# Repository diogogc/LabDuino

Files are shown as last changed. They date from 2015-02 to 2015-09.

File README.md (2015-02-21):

# LabDuino
###EN
This project is my contribution STEM driven classes, in order to help teachers and students on science learning. It's an Arduino based project, feel free to fork or contribute to make it better, or just download, build it yourself or on your classes.

Main Components:

- 1 x Arduino Pro Mini 328 5V;

- 2 x PCF8574P Port expander;

- 1x 16x2 Display;

Voltage Regulator:

I actually followed this instructables for that: <http://www.instructables.com/id/Portable-5V-Regulator/>

I just changed the 78L05 with L7805CV, because i already had a few of them around.

Other

- 8 x 10k Ohms resistor

- 4 x 330 Ohms resistor

- 10k Ohms trimpot

- 2 x 16 pins IC socket (for PCF8574P);

- 16 vias flat 28AWG cable

- 8 x headphone jack (we gonna use it to connect sensors)

For more information, please check the Wiki page.

If you want to become a collaborator, please fill this form:
http://goo.gl/dhk8Ny

###PT-br
Este Projeto é minha contribição para aulas voltadas a STEM, para ajudar professores e alunos no aprendizado de ciências. É um projeto baseado em arduino. Sinta-se livre para fazer fork ou contribuir para fazer este projeto melhor, ou apenas baixe e construa e utilize em suas turmas.

Componentes Principais:

- 1 x Arduino Pro Mini 328 5V;

- 2 x PCF8574P Port expander;

- 1x 16x2 Display;

Regulador de Voltagem:

Eu segui as seguintes instruções: <http://www.instructables.com/id/Portable-5V-Regulator/>

Eu mudei o 78L05 pelo L7805CV porque já tinha alguns aqui comigo.

Outros

- 8 x 10k Ohms resistor

- 4 x 330 Ohms resistor

- 10k Ohms trimpot

- 2 x 16 pinos CI socket (para o PCF8574P);

- Cabo de 16 vias flat 28AWG

- 8 x headphone jack (Usado para conectar os sensores)

Para mais informações, porfavor consulte a pagina Wiki.

Se você quiser se tornar um colaborador, porfavor preencha este formulário:
http://goo.gl/dhk8Ny

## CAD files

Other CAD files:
LaserCutterFiles/LabDuinoBox.skp

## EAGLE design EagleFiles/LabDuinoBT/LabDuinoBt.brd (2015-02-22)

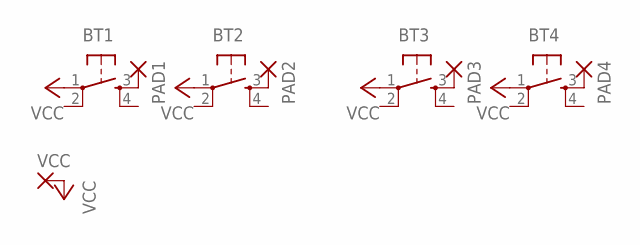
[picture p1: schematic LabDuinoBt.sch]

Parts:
BT1, BT2, BT3, BT4: TAC_SWITCHPTH; TACTILE-PTH
PAD1, PAD2, PAD3, PAD4: 1,6/0,9
VCC: 1,6/0,9

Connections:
unnamed: BT1.3, PAD1.1
unnamed: BT2.3, PAD2.1
unnamed: BT3.3, PAD3.1
unnamed: BT4.3, PAD4.1
VCC: BT1.1, BT2.1, BT3.1, BT4.1, VCC.1

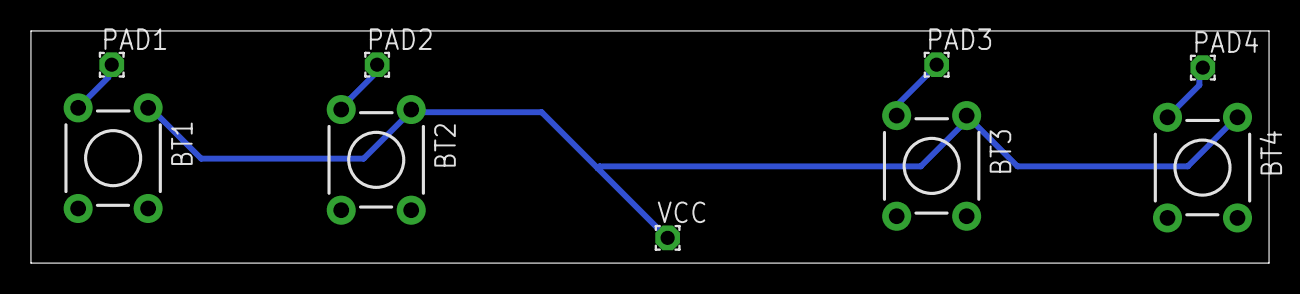
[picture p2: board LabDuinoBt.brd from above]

Board: 2 copper layers, 80.0 x 15.0 mm, 9 parts (0 on the bottom side), 5 nets.

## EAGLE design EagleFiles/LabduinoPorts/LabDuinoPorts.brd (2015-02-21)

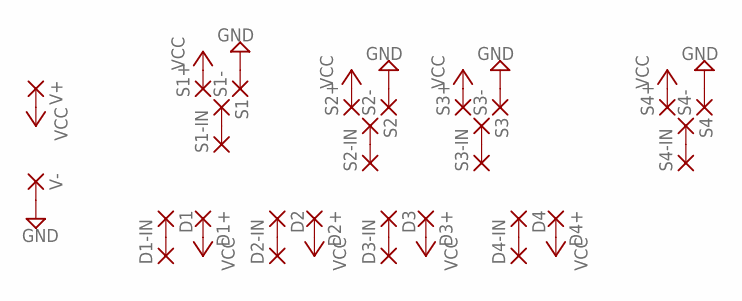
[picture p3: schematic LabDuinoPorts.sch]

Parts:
D1, D1+, D1-IN, D2, D2+, D2-IN, D3, D3+, D3-IN, D4, D4+, D4-IN: 2,54/0,9
S1, S1+, S1-, S1-IN, S2, S2+, S2-, S2-IN, S3, S3+, S3-, S3-IN, S4, S4+, S4-, S4-IN: 2,54/0,9
V+: 2,54/0,9
V-: 2,54/0,9

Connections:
GND: S1-.1, S2-.1, S3-.1, S4-.1, V-.1
unnamed: S1.1, S1-IN.1
unnamed: S2.1, S2-IN.1
unnamed: S3.1, S3-IN.1
unnamed: S4.1, S4-IN.1
unnamed: D1.1, D1-IN.1
unnamed: D2.1, D2-IN.1
unnamed: D3.1, D3-IN.1
unnamed: D4.1, D4-IN.1
VCC: D1+.1, D2+.1, D3+.1, D4+.1, S1+.1, S2+.1, S3+.1, S4+.1, V+.1

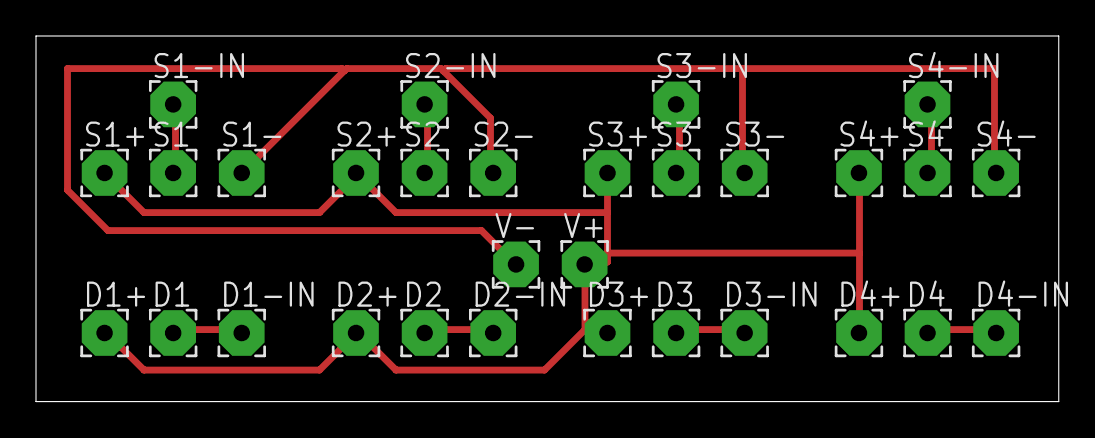
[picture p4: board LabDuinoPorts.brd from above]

Board: 2 copper layers, 56.8 x 20.3 mm, 30 parts (0 on the bottom side), 10 nets.

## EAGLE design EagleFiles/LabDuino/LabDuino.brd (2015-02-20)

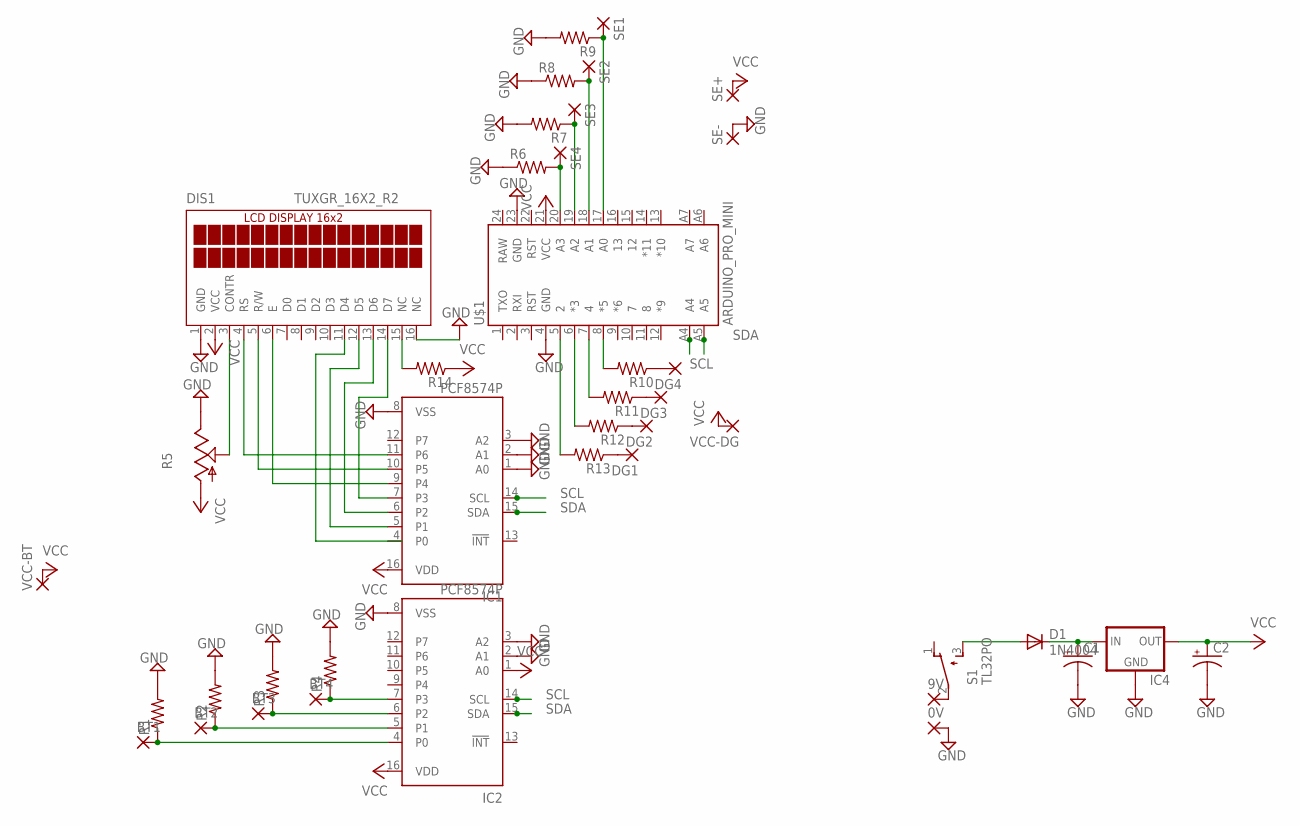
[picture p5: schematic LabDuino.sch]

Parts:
0V, 9V: 2,54/1,1
BT1, BT2, BT3, BT4: 1,6/0,9
C1, C2: CPOL-USE2-4; E2-4
D1: 1N4004; DO41-10
DG1, DG2, DG3, DG4: 1,6/0,9
DIS1: TUXGR_16X2_R2
IC1, IC2: PCF8574P; DIL16
IC4: V_REG_78XX-TO-220; TO-220-ALT
R1, R2, R3, R4, R10, R11, R12, R13, R14: RESISTORPTH-1/6W; 1/6W-RES
R5: TRIM_US-RS3; RS3
R6, R7, R8, R9: R-US_0204/7; 0204/7
S1: TL32PO; TL3XPO
SE1, SE2, SE3, SE4: 1,6/0,9
SE+: 1,6/0,9
SE-: 1,6/0,9
U$1: ARDUINO_PRO_MINI
VCC-BT: 1,6/0,9
VCC-DG: 1,6/0,9

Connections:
10K: BT2.1, IC2.5 (P1), R2.1
GND: 0V.1, C1.-, C2.-, DIS1.1 (GND), DIS1.16 (NC), IC1.1 (A0), IC1.2 (A1), IC1.3 (A2), IC1.8 (VSS), IC2.2 (A1), IC2.3 (A2), IC2.8 (VSS), IC4.GND, R1.2, R2.2, R3.2, R4.2, R5.E, R6.1, R7.2, R8.1, R9.2, SE-.1, U$1.4 (GND), U$1.23 (GND)
unnamed: R6.2, SE4.1, U$1.20 (A3)
unnamed: BT1.1, IC2.4 (P0), R1.1
unnamed: 9V.1, S1.2
unnamed: BT3.1, IC2.6 (P2), R3.1
unnamed: BT4.1, IC2.7 (P3), R4.1
unnamed: R7.1, SE3.1, U$1.19 (A2)
unnamed: DIS1.4 (RS), IC1.11 (P6)
unnamed: DIS1.5 (R/W), IC1.10 (P5)
unnamed: DIS1.6 (E), IC1.9 (P4)
unnamed: DIS1.14 (D7), IC1.7 (P3)
unnamed: DIS1.13 (D6), IC1.6 (P2)
unnamed: DIS1.12 (D5), IC1.5 (P1)
unnamed: DIS1.3 (CONTR), R5.S
unnamed: D1.A, S1.3 (S)
unnamed: C1.+, D1.C, IC4.IN
unnamed: R8.2, SE2.1, U$1.18 (A1)
unnamed: R9.1, SE1.1, U$1.17 (A0)
unnamed: R13.2, U$1.5 (2)
unnamed: R12.2, U$1.6 (*3)
unnamed: R11.2, U$1.7 (4)
unnamed: R10.2, U$1.8 (*5)
unnamed: DG1.1, R13.1
unnamed: DG2.1, R12.1
unnamed: DG3.1, R11.1
unnamed: DG4.1, R10.1
unnamed: DIS1.15 (NC), R14.2
SCL: IC1.14 (SCL), IC2.14 (SCL), U$1.A4
SDA: IC1.15 (SDA), IC2.15 (SDA), U$1.A5
VCC: C2.+, DIS1.2 (VCC), IC1.16 (VDD), IC2.1 (A0), IC2.16 (VDD), IC4.OUT, R5.A, R14.1, SE+.1, U$1.21 (VCC), VCC-BT.1, VCC-DG.1

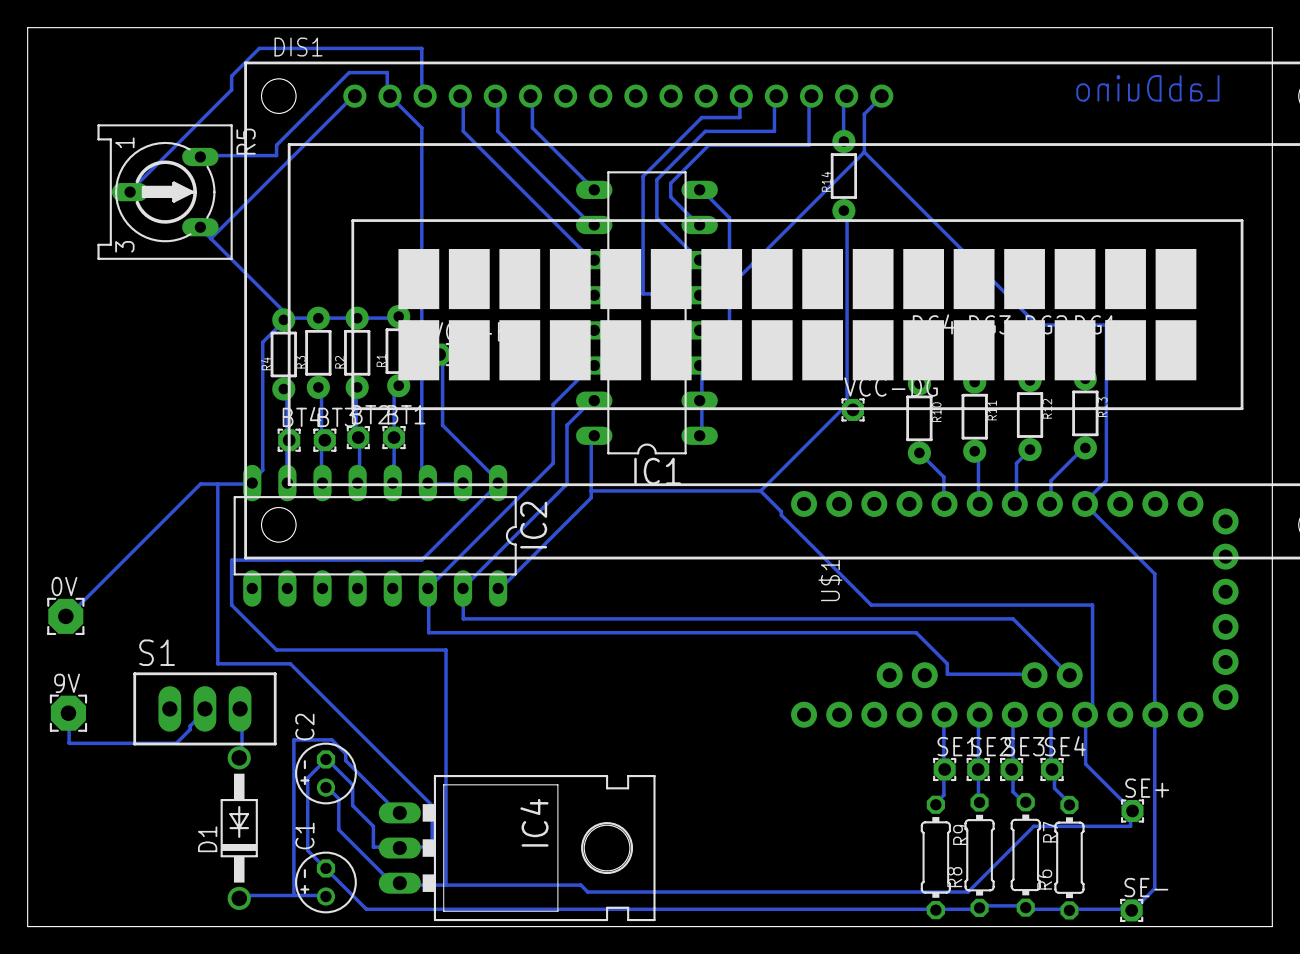
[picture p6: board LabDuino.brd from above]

Board: 2 copper layers, 90.0 x 65.0 mm, 41 parts (0 on the bottom side), 31 nets.

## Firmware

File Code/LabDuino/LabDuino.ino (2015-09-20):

/*
The MIT License (MIT)

Copyright (c) 2015 Diogo Guimaraes Carvalho

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

Mais informacoes (More info):
https://github.com/diogogc/LabDuino
diogo.guimaraes.carvalho@gmail.com

*/

#include <Wire.h>
#include <LiquidCrystal_I2C.h>
#include <SdFat.h>
#include <SPI.h>
#include <AcceleroMMA7361.h>

AcceleroMMA7361 accelero;
SdFat sdCard;
SdFile meuArquivo;
boolean temSd = false;

/*
define portas digitais conectadas aos conectores de fone d1 ao d4
define digital ports wired to phone jacks d1 to d4
*/
#define D1 2
#define D2 3
#define D3 4
#define D4 5
/*
define portas analogicas conectadas aos conectores de fone (s1 ao s4)
define analog ports wired to phone jacks (s1 to s4)
*/
#define S1 A0
#define S2 A1
#define S3 A2
#define S4 A3


LiquidCrystal_I2C lcd(0x20, 16, 2); // set the LCD address to 0x20 for a 16 chars and 2 line display

/*
  InputBotoes
  Buttons Input
*/

/*
  Caracteres personalizados
  Custom Character
*/

// indicator
byte indicador[8] = {
  0b01000,
  0b01100,
  0b01110,
  0b01111,
  0b01110,
  0b01100,
  0b01000,
  0b00000
};
//Home Logo
byte homeLogo[8] = {
  0b00000,
  0b00000,
  0b00100,
  0b01010,
  0b11111,
  0b10001,
  0b10101,
  0b10101
};

// Control flags to check when is on main option or sub options or on experiment
boolean onSubOption = false;
boolean emExpFis = false;
boolean emExpQuim = false;
boolean emExpBio = false;
boolean emExpMat = false;

// Stores user selected options
int currentSelection = 0;
int optionSelected = 0;

// Main menu options
String mainOption1 = "Fisica"; //Physic
String mainOption2 = "Quimica"; // Chemestry
String mainOption3 = "Biologia"; // Biology
String mainOption4 = "Matematica";// Math
String mainOptions[4] = {mainOption1, mainOption2, mainOption3, mainOption4};

// Physics SubOptions
String optionFisica = "Queda Livre";
String optionFisica1 = "Vel. Med.";
String optionFisica2 = "Vel. Inst.";
String subOptionFisica[3] = {optionFisica, optionFisica1, optionFisica2};

// TODO: Add Here all other SubOtions
// TODO: adicione aqui todas as outras subopicoes

/*
  Pega o click do botao (i2c)
  Listen for Button click (i2c)
*/

int pegaInputBotao()
{
  byte x = 0;
  Wire.requestFrom(33, 2);      //Se PCF8574A - mude de 33 para 57 If PCF8574A - change from 33 to 57
  if (Wire.available())    //If the request is available
  {
    x = Wire.read();     //Receive the data
  }
  else
  {
    return 0;
  }
  /*
    Para teste de checagem dos inputs i2c, comente daqui...
    For i2c input check comment from here...
  */

  /*
    Para chegar a estes valores, realizei o teste de input
    To get this values, i've run input check
  */
  if (x == 241) {
    return 1;  // para Baixo Down
  }
  if (x == 242) {
    return 2;  // para cima Up
  }
  if (x == 244) {
    return 3;  // Enter
  }
  if (x == 248) {
    return 4;  // Voltar ESC
  }
  /*
   ...ate aqui
   ...to here
  */

  /*
    Para teste de checagem dos inputs i2c, descomente esta linha
    For i2c input check uncomment this line
  */
  //  return x;
}

/*
  Controle de Paginacao e muda selecao
  Pagging control and change selected option
*/
void navegate(int limit)
{
  if ((currentSelection < (limit - 1)))
  {

    if (pegaInputBotao() == 2) {
      currentSelection += 1;
      lcd.clear();
    }
    else
    {
      if (currentSelection > 0)
      {
        if (pegaInputBotao() == 1) {
          currentSelection -= 1;
          lcd.clear();
        }
      }
    }
  }
  if (currentSelection == (limit - 1))
  {
    if (pegaInputBotao() == 1) {
      currentSelection -= 1;
      lcd.clear();
    }
  }
  if (currentSelection == 0)
  {
    if (pegaInputBotao() == 2) {
      currentSelection += 1;
      lcd.clear();
    }
  }
}
/*
  Pega o click no botao "Enter". Tambem chama os experimentos.
  Listen for enter or Esc buttons. Also Starts Experiment rotines.
*/
void getEnterPress()
{
  if (pegaInputBotao() == 3)
  {
    if (!onSubOption)
    {
      onSubOption = true;
      currentSelection = 0;
      lcd.clear();
    }
    // Ir aos experimentos
    //Go to experiments
    else
    {
      if (emExpFis)
      {
        switch (currentSelection)
        {
          case 0:
            {
              quedaLivre();
              break;
            }
            case 1:
            {
              velociadeMedia();
              break;
            }
//            case 2:
//            {
//              velocidadeInst();
//              break;
//            }
          default:
            break;
        }
      }
    }
  }
  else if (pegaInputBotao() == 4)
  {
    if (onSubOption && (!emExpFis || !emExpQuim || !emExpBio || !emExpMat))
    {
      onSubOption = false;
      currentSelection = optionSelected;
      lcd.clear();
    }
  }
}
/*
  Mostra as opcoes Main Menu
  Shows Main Menu Options
*/
void setSelection()
{
  navegate(4);
  lcd.setCursor(15, 0);
  lcd.write((uint8_t)1);
  switch (currentSelection) {
    case 0: {
        // Escreve a logo Home
        //prints home Logo
        lcd.setCursor(0, 0);
        lcd.write((uint8_t)0);
        lcd.setCursor(2, 0);
        lcd.print(mainOptions[currentSelection]);

        lcd.setCursor(2, 1);
        lcd.print(mainOptions[currentSelection + 1]);
        break;
      }
    case 1: {
        lcd.setCursor(0, 1);
        lcd.write((uint8_t)0);
        lcd.setCursor(2, 0);
        lcd.print(mainOptions[0]);

        lcd.setCursor(2, 1);
        lcd.print(mainOptions[1]);
        break;
      }
    case 2: {
        lcd.setCursor(0, 0);
        lcd.write((uint8_t)0);
        lcd.setCursor(2, 0);
        lcd.print(mainOptions[2]);

        lcd.setCursor(2, 1);
        lcd.print(mainOptions[3]);
        break;
      }
    case 3: {
        lcd.setCursor(0, 1);
        lcd.write((uint8_t)0);
        lcd.setCursor(2, 0);
        lcd.print(mainOptions[2]);

        lcd.setCursor(2, 1);
        lcd.print(mainOptions[3]);
        break;
      }
  }
  optionSelected = currentSelection;
  getEnterPress();
  delay(200);
}
/*
  Mostra o subMenu selecionado
  Shows selected subMenu
*/
void setSubSelection()
{
  int qtdOptions = 0;
  String* mSubOpt;
  /*
    Adicione aqui as subopcoes
    Add here the suboptions
    Neste caso:
    On this case:

    optionSelected = 0 <-- Fisica (Physic)
    optionSelected = 1 <-- Quimica (Chemestry)
    optionSelected = 2 <-- Biologia (Biology)
    optionSelected = 3 <-- Math (Math)

    Note que e a mesma ordem das mainOptions;
    Sinta-se livre para muda-lo para suas nescecidades
    Note that it follows mainOption order;
    Fell free to change it according to your need.
  */
  switch (optionSelected)
  {
    //Fisica
    case 0:
      {
        mSubOpt = subOptionFisica;
        emExpFis = true;
        break;
      }
    //Quimica
    case 1:
      {
        emExpQuim = true;
        break;
      }
    //Biologia
    case 2:
      {
        emExpBio = true;
        break;
      }
    //Math
    case 3:
      {
        emExpMat = true;
        break;
      }
    default: {
        mSubOpt = subOptionFisica;
        break;
      }
  }
  qtdOptions = sizeof(mSubOpt);
  navegate(qtdOptions);
  int i;
  for (i = 0; i < qtdOptions; i = i + 1)
  {

    if (currentSelection == i)
    {
      if (i % 2 == 0)
      {

        lcd.setCursor(0, 0);
        lcd.write((uint8_t)0);
        lcd.setCursor(2, 0);
        lcd.print(mSubOpt[currentSelection]);

        lcd.setCursor(2, 1);
        lcd.print(mSubOpt[currentSelection + 1]);

      }
      else
      {

        lcd.setCursor(0, 1);
        lcd.write((uint8_t)0);
        lcd.setCursor(2, 0);
        lcd.print(mSubOpt[currentSelection - 1]);

        lcd.setCursor(2, 1);
        lcd.print(mSubOpt[currentSelection]);
      }
      getEnterPress();
      break;
    }
  }
  delay(200);
}

/*
Metodos dos experimentos aqui
Experiments methods here
*/

void velociadeMedia()
{
  /*
  setar portas utilizadas
  set used ports
  */
  pinMode(D1, INPUT); //Sensor IR
  pinMode(D3, INPUT); //Sensor IR
  pinMode(D2, OUTPUT); //Emissor IR (Emiter)
  pinMode(D4, OUTPUT); //Emissor IR (Emiter)

  /*
    Parametros
    Parameters
  */

  float start, finish, elapsed, elapsedInSec;
  float velMed;
  float distancia ;

  boolean pegouDistancia = false;
  boolean started = false;
  boolean finished = false;
  lcd.clear();
  while (true)
  {
    if (!pegouDistancia)
    {
      lcd.setCursor(0, 0);
      lcd.print("qual dist em M?");
      lcd.setCursor(0, 1);
      lcd.print(distancia);

      if (distancia > 0.1)
      {
        if (pegaInputBotao() == 2)
        {
          distancia = distancia - 0.1;
        }
        else if (pegaInputBotao() == 1)
        {
          distancia = distancia + 0.1;
        }
        else if (pegaInputBotao() == 3)
        {
          pegouDistancia = true;
          lcd.clear();
        }
      }
      else
      {
        if (pegaInputBotao() == 1)
        {
          distancia = distancia + 0.1;
        }
      }
    }
    else
    {
      if((digitalRead(D2)!=HIGH) && (digitalRead(D4)!=HIGH))
      {
        digitalWrite(D2,HIGH);
        digitalWrite(D4,HIGH);
      }
      if (!started && !finished) {
        lcd.setCursor(0, 0);
        lcd.print("esperando carro");
        lcd.setCursor(0, 1);
        lcd.print("passar P inicial");
        if(digitalRead(D1)==HIGH)
        {
          started = true;
          start=millis();
          lcd.clear();
        }
      }
      else
      {
        if (started && !finished) {
          lcd.setCursor(0, 0);
          lcd.print("Iniciou!");
          lcd.setCursor(0, 1);
          lcd.print("Tempo:");
          lcd.print((millis() - start)*0.001);
          
          if(digitalRead(D3)==LOW)
          {
            finished = true;
            finish=millis();
            lcd.clear();
          }
        }
        else if(started && finished)
        {
          elapsed=finish-start;
          elapsedInSec = elapsed *0.001;
          velMed = distancia / elapsedInSec;
          lcd.setCursor(0, 0);
          lcd.print("Terminou ");
          lcd.print("T:");
          lcd.print(elapsedInSec);
          lcd.print("s");
          lcd.setCursor(0, 1);
          lcd.print("Vel :");
          lcd.print(velMed);
          lcd.print(" m/s");
        }

      }
    }
    if (pegaInputBotao() == 4)
    {
      if (pegouDistancia)
      {
        pegouDistancia = false;
      }
      else {
        break;
      }
    }
    delay(100);
  }
  lcd.clear();
}
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

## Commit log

2015-02-11 Arquivos Eagle e Codigo
    [LabDuino.brd, LabDuino.sch, LabDuinoBt.brd, LabDuinoBt.sch]
2015-02-20 Board Update
    [LabDuino.brd, LabDuino.sch]
2015-02-20 Better folder names
    [LabDuino.brd, LabDuino.sch, LabDuinoBt.brd, LabDuinoBt.sch]
2015-02-20 Sensor Ports / Button board adjustment
    [LabDuinoBt.brd, LabDuinoBt.sch, LabDuinoPorts.brd, LabDuinoPorts.sch]
2015-02-20 Laser Cutter Files
    [Arduino Diogo.skp]
2015-02-20 Name correction
    [LabDuinoBox.skp]
2015-02-21 Eagle LabDuinoPorts Update
    [LabDuinoPorts.brd, LabDuinoPorts.sch]
2015-02-21 LabDuino Box Update
    [LabDuinoBox.skp]
2015-02-22 Button Board UpDate
    [LabDuinoBt.brd, LabDuinoBt.sch]

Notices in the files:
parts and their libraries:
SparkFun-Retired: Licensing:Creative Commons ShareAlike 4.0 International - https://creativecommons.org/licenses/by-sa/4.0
